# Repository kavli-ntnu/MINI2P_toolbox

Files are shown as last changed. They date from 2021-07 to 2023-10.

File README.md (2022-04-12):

# MINI2P_toolbox 
 
## Project:

MINI2P freely-moving calcium imaging and spatial tuning analysis

## Description: 

MINI2P_toolbox includes the codes, softwares, 3D models, protocols, and etc. for buidling and using MINI2P to do freely-moving recording. MINI2P is an open-source miniature 2-photon microsocpe for fast high-resolution calcium imaging in freely-moving mice, published in Zong, et al.,"Large-scale two-photon calcium imaging in freely moving mice (2022)". With the materials provided in this toolbox, people can assemble, test the MINI2P system, set up the animal tracking system, process the MINI2P imaging data, extract neuronal activity from single cells, and combine the neuronal activity data and the tracking data together for user-depedent downsteam analysis. The multi-FOV stitching software is also included. The codes for most of the anaylsis (grid cells, place cells, etc) in the paper "Large-scale two-photon calcium imaging in freely moving mice (2022)" are also provided.

## Contents: 

1) [Hardware](Hardware)

      [3D models (and 2D drawings for custom components)](Hardware) of all components for bulding a complete MINI2P system.


2) [Protocols](Protocols)

    a) [P1–Shopping and Machining list](https://github.com/kavli-ntnu/MINI2P_toolbox/blob/960fcab65f2849e5c8f486b81061c7c759f8e879/Protocols/P1%20-%20Shopping%20&%20Machining%20List%20.pdf). This document lists each essential component with the supplier, the product name, the model (or item reference) and its approximate price in Euro. 2D Drawings and 3D models of most components are available [here](https://github.com/kavli-ntnu/MINI2P_toolbox/tree/main/Hardware) .

    b) [P2-System building protocol](https://github.com/kavli-ntnu/MINI2P_toolbox/blob/main/Protocols/P2%20-%20System%20building%20protocol%20.pdf). This protocol includes all steps to assemble a MINI2P system. Each Protocol starts with a short-list of main reagents and tools needed, followed by an overview schematic of the module, and  a table with the main products.
       HC-920 assembly building and laser coupling video tutorial can be found on the [link](https://www.youtube.com/watch?v=HjAtoPbDu8E).    

    c) P3–Miniscope assembly protocol. How to assemble a MINI2P microscope is described in this protocol. Assembly tutorial video can be found on the [link](https://youtu.be/I0aYfi8GrIc). 

3) [Software](Software) 
      
      a) One scanimage Machine Data File (MDF) for [2000Hz MEMS-L scanner](Software/SI%20settings/Machine_Data_File_2000Hz.m). A second file for [5600Hz MEMS-F scanner](https://github.com/kavli-ntnu/MINI2P_toolbox/blob/main/Software/SI%20settings/Machine_Data_File_5600Hz.m)
      
      b) An example [Suite2P settings](Software/Suite2P%20options/GCaMP6S_P2_C1_7.25Hz_MEC.npy).
      
      c) Two DLC model configuration files:
      * [DLC1](Software/DLC%20model%20options/DLC1.yaml),
      * [DLC2](Software/DLC%20model%20options/DLC2.yaml),
      
      More details in [Documents](Documents/DeepLabCut-trained-Models.md).
      
      d) [AnimalTracker.vi](Software/AnimalTracker): a Labview program for recording animal behaviors and synchronizing the tracking camera recording with the MINI2P imaging. More details in [Documents](Documents/AnimalTracker.vi.md)
      
      e) [MINI2P SI device](https://github.com/kavli-ntnu/MINI2P_toolbox/tree/main/Software/MINI2P%20SI%20Device): Briefly, this device enables users to measure MINI2P distortion in different planes, do fast data correction, and register MINI2P system information in ScanImage software. And all this information is saved in Tiff header now.  Video tutorial can be found on the [link](https://youtu.be/DlftmRX5ty0).  More details in [Readme](https://github.com/kavli-ntnu/MINI2P_toolbox/blob/main/Software/MINI2P%20SI%20Device/Readme_20220322.docx)

4) [Analysis](Analysis)

      a) [Pipelines](/Analysis/Pipeline) for spatial tuning analysis included in the paper (grid cells, place cells,etc).

      b) [NATEX.mlapp](/Analysis/Applications/NATEX): Nat Explorer, an application to load, process and preview the neuronal activity data (from the Suite2P output) and the tracking data (from the DLC output). It also combines the neuronal activity data and tracking data into the NAT.mat (Neuron Activity aligned with Tracking Matrix) and put all necessasy information into ExperimentInformation.mat for the user-specific downsteam analysis. More details in [Documents](Documents/NATEX.mlapp.md) 
      

      c) [StitchingChecker.mlapp](Analysis/Applications/StitchingChecker): an application to stitch multiple FOV recorded from different positions of the cortext. It can load in wide-field image as a reference for FOV alignment and can also take the retinotopic mapping result in for identifying different visual cortices. The precise alginment of FOVs is confirmed by 
      
      * overlapping of the landmarks between FOVs and the wide-field image, or between neighbouring FOVS; 
        
      * peak cross-correlation between FOVs and the wide-field image, or between neighbouring FOVs;
        
      * overlapping of the repeated cells in neighbouring FOVS. We also found this application can be used to register imagings recorded in multiple days. 
          
      More details in [Documents](https://github.com/kavli-ntnu/MINI2P_toolbox/blob/main/Documents/StitchingChecker.mlapp.md)
     

     d) [DistortionCleaner.mlapp](Analysis/Applications/DistortionCleaner)： an application to elimiate the scanning distortion of MINI2P imaging, calibrate FOV and pixel size, and generate transform matrix. This program works similar to the ScanImage plugin “MINI2P distortion detecotion", but can work without installing Scanimage. Note that since the release of MINI2P SI Device in March, 2022, this function is not in use or maintenance any more. Users can still install and try it but we will not provide any support or bug-fix. More details in [Documents](Documents/DistortionCleaner.mlapp.md)
     

5) [Documents](Documents)

    a) [Requirements](Documents/requirements.md): A list of the non-optical components necessary to build and use a MINI2P system, including licencsed software requirements. 
    
    b) [How-to](Documents/readme.md): A set of more detailed how-to documentation about how some components of the system work. 

## Usage:

  Applications NATEX, StitchingChecker and DistortionCleaner were written with Matlab app designer. In order to use these software, please press "open” in the home toolstrip of Matlab, select the software, wait until the app designer interface pops out, and then press "run". Some details in how to use each application is provided under [Documents](Documents/readme.md)

## Credits: 

This repository was created by Weijian Zong and maintained by the [Moser group](https://www.ntnu.edu/kavli/moser-group#/view/about) at Kavli Institute for Systems Neuroscience. It has benefitted from the inputs of all authors of the paper Zong, et al.,"Large-scale two-photon calcium imaging in freely moving mice," _Cell_(2022). Sections of the analysis code are based on the [Behavioural Neurology Toolbox](https://bitbucket.org/cnc-ntnu/bnt), (c) Vadim Frolov 2018.

MINI2P is a complete open-source project, we encourage people to use, test, modify and further develop this toolbox. If you have any questions or suggestions, or find any bugs in the codes, please contact us or submit an issue. If you use the code or data, please cite us!

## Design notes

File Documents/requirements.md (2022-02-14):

# Requirements for the mini2p toolbox

## Hardware

Substituting alternative, comparable, pieces of hardware is generally possible. Modifications to the software will usually be required if so.

### Microscope

A complete bill of materials can be provided upon request. Details of specific hardware components of the microscope are discussed in the associated publication:

> W. Zong *et al*, "Large-scale two-photon calcium imaging in freely moving mice". [BioRXiv (2021)](https://doi.org/10.1101/2021.09.20.461015)

A single computer workstation is required for experiment control. Experimental control is not particular demanding of computing resources:
* Windows 10 x64
* Spare PCIe 3 x8 interface
* Spare PCIe 6-pin power connector

Post-recording imaging analysis via Suite2P and DeepLabCut is more demanding. Post-recording analysis does not need to take place on the same computer. 
* Version 11 Cuda compatible graphics card with >8GB vRAM
* Minimum 4GB RAM per CPU core, recommended 8GB.
* Minimum 4 cores. 

## Software

### Recording

* Matlab 2020b or more recent
  * [Mathworks](https://se.mathworks.com/)
* LabView 2020 or more recent
  * [National Instruments](https://www.ni.com/en-no/shop/labview.html)
  * [Anaconda](https://www.anaconda.com/products/individual)
* ScanImage 2020 Basic or more recent
  * The Free edition does not provide the necessary tools
  * [Vidrio](https://vidriotechnologies.com/compare-scanimage-version/)
* vDAQ RDI driver 2019-11-20 or more recent
  * SDK for the vDAQ interface card
  * [Vidrio](https://vidriotechnologies.com/drivers)
* Pylon 6.2.0 or more recent
  * Camera controller software for the Basler camera series
  * [Basler](https://www.baslerweb.com/en/sales-support/downloads/software-downloads/)
* PMT2100 4.0 or more recent
  * SDK for the Thorlabs PMT2100 photomultiplier tube
  * [Thorlabs](https://www.thorlabs.com/software_pages/ViewSoftwarePage.cfm?Code=PMT)

### Postprocessing

* Matlab 2020b or more recent
  * [Mathworks](https://se.mathworks.com/)
* Python 3.8 or more recent
  * Due to Suite2P's requirements, Anaconda and the Conda package manager are recommended
* DeepLabCut 2.2.0 or more recent
  * MachineMarkerless subject tracking
  * [Mathis Lab](http://www.mackenziemathislab.org/deeplabcut)
* Suite2p v0.10.0 or more recent
  * Two-photon imaging processing
  * [Pachitaru Lab](https://github.com/MouseLand/suite2p)

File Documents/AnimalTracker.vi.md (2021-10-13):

## Program location: 
MINI2P_toolbox/Software/AnimalTracker/
## Description: 
AnimalTracker.vi is a Labview program for recording animal behaviors, and synchronizing the tracking to the MINI2P imaging using a Basler camera. Currently, it was well validated by using camera acA2040-90um-NIR (https://www.baslerweb.com/en/products/cameras/area-scan-cameras/ace/aca2040-90um/). More validation will be published soon.
## Hardware requirement: 
1) Basler camera (recommend: [aca2040-90um](https://www.baslerweb.com/en/products/cameras/area-scan-cameras/ace/aca2040-90um/));
2) Basler camera [I/O cable](https://www.baslerweb.com/en/products/vision-components/cable/basler-gp-i-o-cable-hrs-6p-open-p-10-m/);
3) Basler cable [USB 3.0 Micro B](https://www.baslerweb.com/en/products/vision-components/cable/basler-cable-usb-3-0-micro-b-sl-a-p-3-m/);
## Software requirement: 
1) [NI-MAX](https://www.ni.com/en-no/support/downloads/drivers/download.system-configuration.html#371210)(20.0 or newer)
2) [Labview](https://www.ni.com/en-no/support/downloads/software-products/download.labview.html#369643)(2020 or newer)];
3) [NI-IMAQ](https://www.ni.com/en-no/support/downloads/drivers/download.vision-acquisition-software.html#367318);
3.1) [NI-IMAQmx](https://www.ni.com/en-no/support/downloads/drivers/download.ni-daqmx.html#409845);
3.2) [NI-IMAQdx](https://www.ni.com/en-no/support/downloads/drivers/download.vision-acquisition-software.html#367318);
4) (optional)[Pylon](https://www.baslerweb.com/en/sales-support/downloads/software-downloads/software-pylon-6-2-0-windows/) (6.2.0 or newer);
## Wiring:
To establish the correct camera wiring, first select Pins 2 and 5 of I/O cable which are Opto-coupled I/O input line and its ground, respectively. On the I/O cable, pins 2 and 5 are assigned as Pink and Grey, respectively. Link them with a BNC connector and plug the I/O cable from the camera to the vDAQ frame clock channel (one of the digital channels, in this case D3.7). See Fig. (1) for illustration.
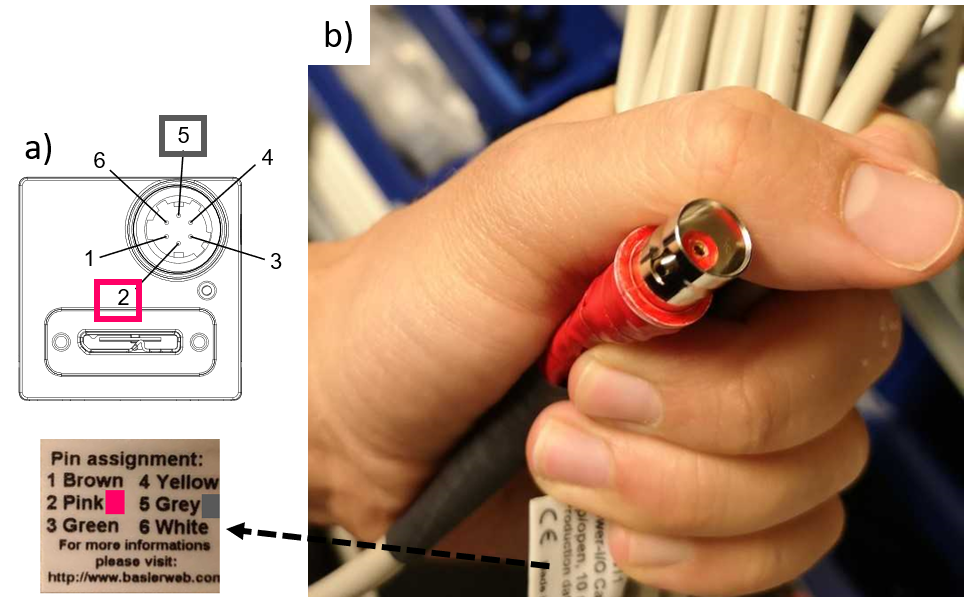
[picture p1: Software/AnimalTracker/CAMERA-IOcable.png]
Schematic of I/O cable pins and labelling used to connect the Animal Tracker camera


The Basler camera is working in External Trigger Mode, meaning it starts as soon as it gets a signal (0-5V) via input cable from the vDAQ (Start focus or grab in Scan Image, which sets up the Animal Tracker).
## Installation: 
The necessary drivers are those mentioned in Software Requirements from NI-MAX and NI-IMAQ. Pylon drivers are not needed, unless one wishes to visualize the camera using Pylon Software. In that case, USB 3.0 drivers should be installed.
### main pragram
To start-up, open the Virtual instrument application (.vi file) entitled "AnimalTracker.vi", and a graphical user interface will display as follows:

## GUI:
![Schematic of Animal Tracker GUI overview]
(https://github.com/kavli-ntnu/MINI2P_toolbox/blob/4a45033ba603d2f39251690c86131b548938de0d/Software/AnimalTracker/AnimalTracker-overview.png)

## Usage:
### change the default frame size, frame rate, exposure time and gain
1. On the same Directory where the imaging files are going to be saved, create an empty text file (in this case, "1.txt"). 
2. On the top left panel (see nr 1), select that text file created.
3. Chose Trigger Mode "External" and update frame rate (14.5 Hz) as well as other parameters as shown.
4. Finally, on the left bottom part, choose the camera type "1" for bottom and "2" for Top, and other relevant information which is going to be attached to a .csv file as:

###
## Output:

## .tiff to .mp4 conversion

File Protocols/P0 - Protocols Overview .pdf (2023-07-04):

## Protocols Overview

### P1 – Shopping and Machining list

This document lists each essential component with the supplier, the product name, the model (or item reference) and its approximate price in Euro. 2D Drawings and 3D models of
most | components | are | available | on | Github | (https://github.com/kavli-
ntnu/MINI2P_toolbox/tree/main/Hardware). (https://github.com/kavli-ntnu/MINI2P_toolbox/tree/main/Hardware)

### P2 – System building protocol

This protocol includes all steps to assemble a MINI2P system. Each Protocol starts with a short-list of main reagents and tools needed, followed by an overview schematic of the module, and a table with the main products.
HC-920 assembly and laser coupling video tutorial can be found on the link: https://www.youtube.com/watch?v=vo_EgYPYI24&list=PLonWNO9SywvJXpIgQEp6jQMSh_jrn_jPU&index=3&t=4s. (https://www.youtube.com/watch?v=vo_EgYPYI24&list=PLonWNO9SywvJXpIgQEp6jQMSh_jrn_jPU&index=3&t=4s)

### P3 – Miniscope assembly protocol

How to assemble a MINI2P microscope is described in this protocol. Assembly tutorial video can be found on the link: https://www.youtube.com/playlist?list=PLonWNO9SywvJXpIgQEp6jQMSh_jrn_jPU.

### GFB assembly protocol

This protocol describes the steps to assemble the GRIN-end fiber bundle (GFB), which replaces the tapered fiber bundle (TFB) as the main fiber collecting and relaying the emission signal to the detection module.

### MEMS wires and mirror protocol

This protocol includes the main steps for MEMS wires assembly and soldering of the MEMS mirror flex cable. Soldering MEMS flexcable can be found on the link: https://www.youtube.com/watch?v=ghV1DY1aKAA&list=PLonWNO9SywvJXpIgQEp6jQMSh_jrn_jPU&index=1 (https://www.youtube.com/watch?v=ghV1DY1aKAA&list=PLonWNO9SywvJXpIgQEp6jQMSh_jrn_jPU&index=1)

The MINI2P video tutorial package can be found on the link: https://www.youtube.com/playlist?list=PLonWNO9SywvJXpIgQEp6jQMSh_jrn_jPU

Besides the video-tutorials above, it also includes:
- ScanImage tutorial:
https://www.youtube.com/watch?v=uUZ1o5XFiwU&list=PLonWNO9SywvJXpIgQEp6jQMSh_jrn_jPU&index=2&t=714s (https://www.youtube.com/watch?v=uUZ1o5XFiwU&list=PLonWNO9SywvJXpIgQEp6jQMSh_jrn_jPU&index=2&t=714s)
- SI device for distortion, detection, and correction: https://www.youtube.com/watch?v=4hNTMCyMdrM&list=PLonWNO9SywvJXpIgQEp6jQMSh_jrn_jPU&index=5&t=59s (https://www.youtube.com/watch?v=4hNTMCyMdrM&list=PLonWNO9SywvJXpIgQEp6jQMSh_jrn_jPU&index=5&t=59s)

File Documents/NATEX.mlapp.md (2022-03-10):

## Application location:

[NATEX.mlapp](https://github.com/WeijianZong/MINI2P_toolbox/tree/main/Analysis/Applications/NATEX)
## Description:
One recording in a freely-moving experiment using MINI2P system usually includes one or multiple MINI2P calcium imaging files (tiff stack) generated by [ScanImage](https://vidriotechnologies.com/scanimage/) and one or multiple animal tracking videos generated by tracking camera recording software, such as [AnimalTracker](https://github.com/WeijianZong/MINI2P_toolbox/wiki/AnimalTracker.vi) or [Pylon](https://www.baslerweb.com/en/sales-support/downloads/software-downloads/software-pylon-6-2-0-windows/). Becuase the MINI2P imaging and tracking video recording in our system is [hardware-level synchronized](https://github.com/WeijianZong/MINI2P_toolbox/wiki/NATEX.mlapp#synchronization-and-frame-rate), the synchronization data is not required.

In order to implement quantitative analysis for real neuroscience studies, individual cells' anatomical and activity information, and animal behavior including trajectory, speed, and head direction need to be extracted from the raw imaging tiff files and tracking videos, respectively. 

First of all, we use [Suite2P](https://suite2p.readthedocs.io/en/latest/) to do cell segmentation, signal extraction, and signal deconvolution from raw calcium imaging tiff stack, and [DeepLabCut](https://suite2p.readthedocs.io/en/latest/) to extra animal`s body parts, like ears, body center, tail base, and etc., from raw animal tracking video. Still, the output of Suite2P and DeepLabCut can not be directly used for biology analysis until a more meaningful, highly extracted and integrated, and easy-to-understand data format is generated. And a powerful data visualization tool for non-programming-expert to easily present and investigate these data before going into a more complex analysis is also required. NATEX.mlapp was developed for these purposes. It has four major functions:

1) Process [Suite2P output](https://github.com/WeijianZong/MINI2P_toolbox/wiki/NATEX.mlapp#suite2p-output): take the output from Suite2P, calculate dF/F, significant transients, and SNR, clear up the deconvolved signal, detect repeated cells in multiplane imaging data, and finally package the processing information and save processed neuron activity data.
2) Process [DeepLabcut output](https://github.com/WeijianZong/MINI2P_toolbox/wiki/NATEX.mlapp#deeplabcut-output): Take the output from DeepLabCut, calculate head/body position, speed, direction using user-selected tracking models, combine or split multiple recording sessions, and finally package the processing information and save processed tracking data. 
3) Integration: combine the processed neuron activity data and tracking data with a user-defined alignment strategy, package the combination information, and save the combined data. 
4) Data Visualization: provide multiple useful functions to view the neuronal activity (dF/F, significant transients, or deconvolved signal), different types of anatomical cell map, MINI2P imaging projection, animal trajectory derived by head or body (coded by position, speed, direction), the spatial tuning plots ( calcium event/position plot, activity map, calcium event/direction/position plot, directional tuning), etc.
The simplified data-flow chart and NATEX major functions are shown below:

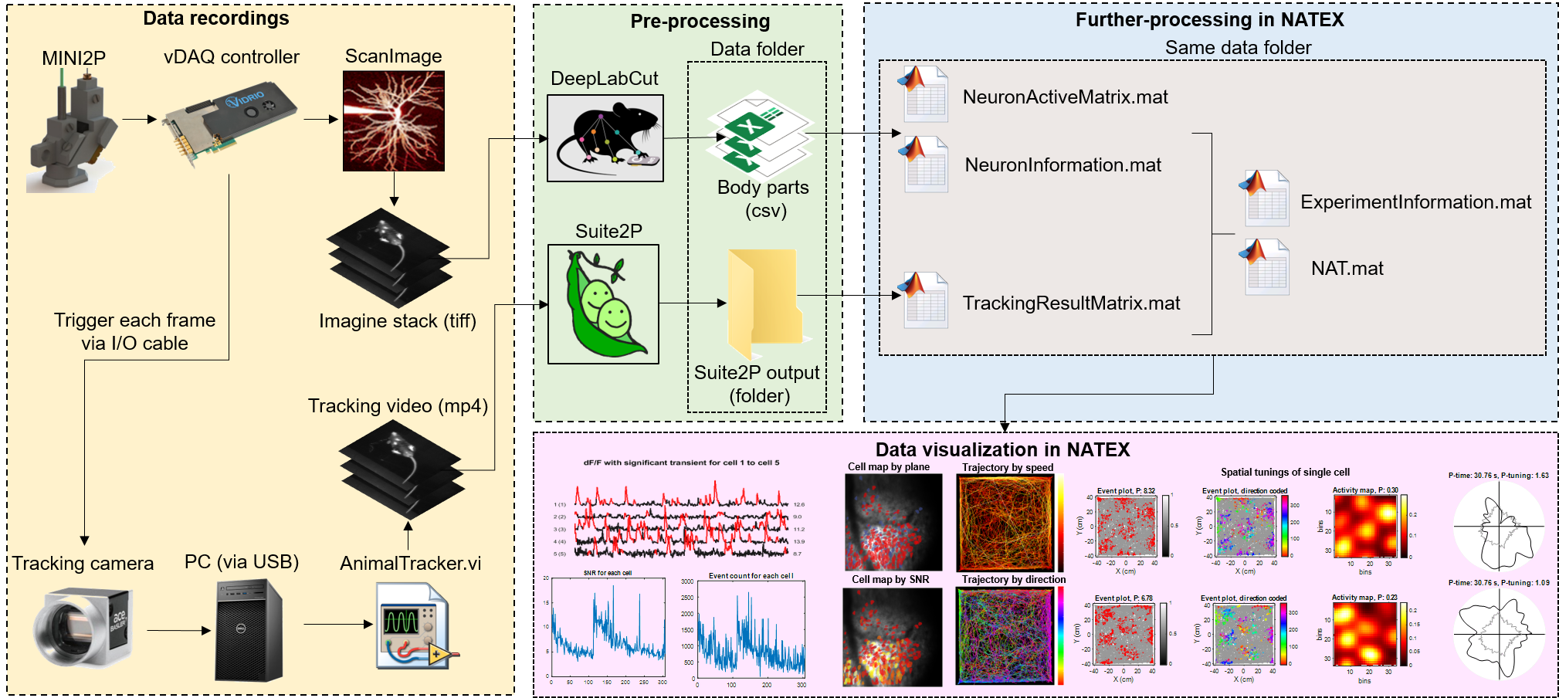
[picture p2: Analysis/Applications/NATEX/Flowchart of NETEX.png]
Schematic of the data flow from the raw data recording to the output of NATEX


NATEX.mlapp is highly modularized so you can input, process, view, output, and reload (processed) neuronal activity data, tracking data, or combined data independently. 

The Python version of NATEX will be published in the first KISN International MINI2P workshop in 2022.

## Installation:

### Matlab and toolbox
The app was written with Matlab 2020a, but should work with any newer version. It uses the Statistics and Machine Learning Toolbox, the DSP System Toolbox and the Curve Fitting Toolbox, which need to be installed before running the applications.

### Install application
There are two ways to install the application.

First way is to install the raw codes which gives you the right to modify the function:

Download or clone the whole repository in a local folder. Open Matlab, press "set path” on home toolstrip, then press “add with subfolders...", navagate to the location of \MINI2P_toolbox\MINI2P_toolbox\AnLysis, press "select folder", and finally, "save" the current path.

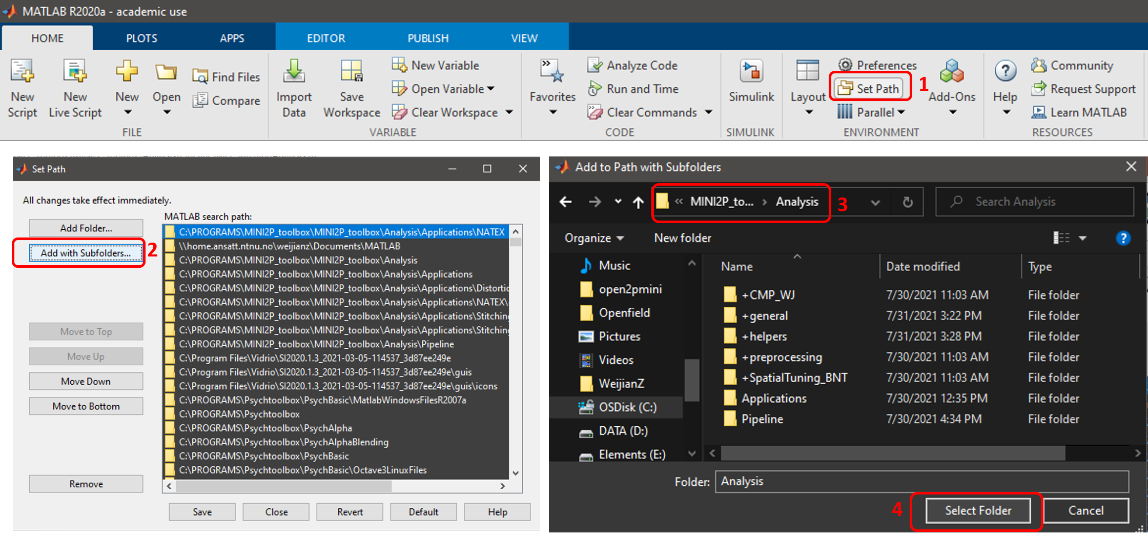
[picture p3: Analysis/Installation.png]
Installation


Second way is to install the app into the Matlab toolboxes which makes the most convinient way to call it. But you can not see or change the codes:

### Install ScanImage
In order to read out and save the ScanImage tiff header (the function "Save SI Information"), you need to install ScanImage on the same computer too. The free version will work well. Follow their [instruction](https://vidriotechnologies.com/scanimage/) for installation.

## Input format and organization:

### Directory structure
All recordings belong to one experiment should be put in one "data folder". An experiment can include multiple sessions and in each session, the raw data usually includes one tiff-stack file from MINI2P recording (output from ScanImage) and one tracking video (.AVI). For analyzing neuronal activity data, you should first run Suite2P analysis on your raw tiff files. Suite2P will automatically combine all tiff files in the "data folder" together to extract the cell signal and generate a single output folder called "suite2p". Folder "suite2p" is the only thing NATEX.mlapp needs to process the neuronal activity data. Therefore, do not change the name of this folder after it is generated by Suite2P. In addition, important to make sure that the option "save_mat" is 1 and the option "combined" is 1 when you run the Suite2P analysis. If you want to also extract and output the ScanImage tiff header (when the function "Save SI Information" is enabled), keep the raw tiff files in the "data folder" too. For analyzing tracking data, you will first run DeepLabCut (or other method or software) to extract the body part position. DeepLabCut will generate one set of results for each video (or session). NATEX.mlapp only looked for and takes the CSV files that include all body-part tracking results to do the tracking analysis. In other words, as soon as you can generate CSV files with the same format as DeepLabCut, they can be read by NATEX.mlapp for analysis. The number of sessions is decided by the number of tracking files (.csv) the user selects. 

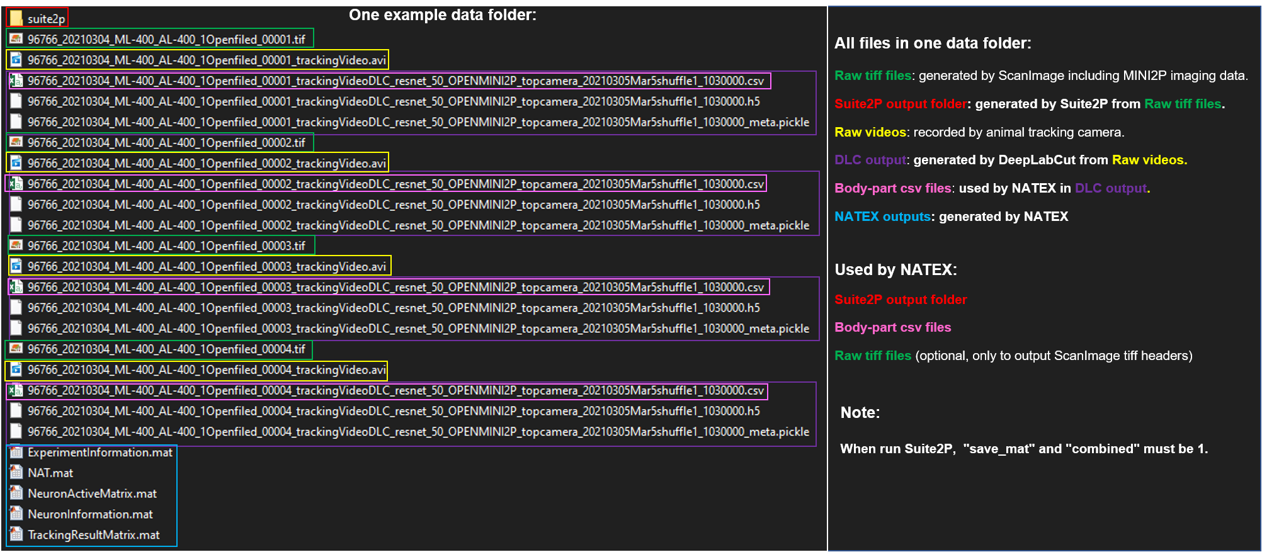
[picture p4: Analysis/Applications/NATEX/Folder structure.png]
Folder Structure


### Session definition
### Modularity
NATEX is coded with high modularity which means the neuronal activity analysis and tracking analysis are quite independent. Therefore, it does not require all kinds of input to run specific analyses. For example, if you select the analysis type as " [Only MINI2P](https://github.com/WeijianZong/MINI2P_toolbox/wiki/NATEX.mlapp#only-analyze-calcium-activity-data-mini2p-imaging) ", you only need to have the Suite2P output folder. And if you select " [Only tracking](https://github.com/WeijianZong/MINI2P_toolbox/wiki/NATEX.mlapp#only-analyze-tracking-data) ", you only need the body-part CSV files. This is useful for some pilot experiments such as head-fixed test recordings or pure behavior studies in which, tracking video or MINI2P imaging files is not applicable, respectively.

## Output format and organization:
In total, NATEX will generate five output files. NeuronActivityMatrix.mat and NeuronInformation.mat are generated if the analysis type is "Only MINI2P" "MINI2P+tracking" or "Complete pipeline". TrackingResultMatrix.mat is generated if the analysis type is "Only Tracking ", "MINI2P+tracking" or "Complete pipeline". NAT.mat and ExperimentInformation.mat are generated if the analysis type is "Complete pipeline", or manually execute the function "generate NAT!". All these files are saved in the same data folder.

### NeuronActivityMatrix.mat
NeuronActivityMatrix.mat is generated after the neuronal activity analysis part in analysis type "Only MINI2P" "MINI2P+tracking" or "Complete pipeline" is finished. It included several cell-by-cell signal traces described in detail below: 
### NeuronInformation.mat
NeuronInformation.mat is also generated after the neuronal activity analysis part in analysis type "Only MINI2P" "MINI2P+tracking" or "Complete pipeline" is finished. It included cell footprints, SNR, event counting, processing parameters, and all other useful analysis information other than the signal traces that are saved in NeuronActivityMatrix.mat already. Described in detail below: 
### TrackingResultMatrix.mat
TrackingResultMatrix.mat is generated after the tracking analysis part in analysis type  "Only Tracking ", "MINI2P+tracking" or "Complete pipeline" is finished. It included the head (or body if selected) position, direction and speed information, tracking processing parameters,and all other useful analysis information. This is the only output in tracking analysis part. Described in detail below: 
### NAT.mat
NAT.mat is generated after the neuronal activity data and tracking data combination part in analysis type "Complete pipeline", or manually executed function "generate NAT!" is finished. It is a matrix that combines cell-by-cell neuronal activity data and animal tracking data.Described in detail below: 
### ExperimentInformation.mat
ExperimentInformation.mat is also generated after after the neuronal activity data and tracking data combination part in analysis type "Complete pipeline", or manually executed function "generate NAT!" is finished. Most of the information saved here are copied from NeuronInformation.mat and TrackingResultMatrix.mat. But it also includes the neuronal activity data and tracking data combination and alignment information that is unique here. Described in detail below: 

## GUI:
### Overview
There are 11 permanent panels on GUI and a pop-up will appear when a certain preview button is pressed (described in detail below). Currently, all options and parameters will be saved in output data files (.mats) and updated automatically when processed data is loaded in. In the future version, NATEX will allow the user to save and load in analysis options and parameters without specific processed data.
### "Data input" panel
In this panel, user selects the desired analysis type and the data folder. In the future version, user can also save and load in analysis options and parameters in this panel.
1. "Analysis type": a drop-down allows users to select analysis type.
2. "Select data folder and DLC output": when press this button, a folder-selecting dialog box appears for the user to select the data folder. if the analysis type is "Only Tracking ", "MINI2P+tracking" or "Complete pipeline", a second dialog box appears after the data folder is selected, for the user to select tacking CSV files. Users should select "all" csv files that they want to analyze and combine with neuronal activity data.
### "Control" panel
In this panel, user controls the start and abort of the analysis.
1. "Run analysis!": start the analysis based on user-selected analysis type.
2. "Abort analysis": manually abort the analysis. Attention! You may get some incomplete results or output when aborting the analysis. Errors may also appear if you use other functions after aborting an analysis. Therefore, always run the analysis again after you abort the last analysis.
3. "Close all figures": all pop-ups will be closed.
### "Options for neuronal activity analysis" panel
In this panel, user needs to decide several options for processing and analyzing the neuronal activity data. The reason and reference for these parameters can be found in the original paper (Zong, et.al, 2021).
1. "Moving window": The time window to calculate the local standard deviation of the raw fluorescence. This local standard deviation is then used to compute the baseline fluorescence (F-zero). See [ΔF/F](https://github.com/WeijianZong/MINI2P_toolbox/wiki/NATEX.mlapp#%CE%94ff) calculation for details.  Default: 30s.
2. "Transient lasting": the temporal lasting threshold for a transient to be called a "significant transient". See [Significant transient](https://github.com/WeijianZong/MINI2P_toolbox/wiki/NATEX.mlapp#significant-transient) calculation for details. It depends on the calcium indicator dynamics and the signal quality. Default: 0.75s for GCaMP6s transgenic mice.
3. "Lowpass filter": the cut-off frequency of a low-pass filter applied on cell signal (ΔF/F) for calculating the cross-correlation between cells. It is not applied to the output data or any downstream analysis. Default: 2Hz.
4. "Neuropil correction": neuropil coefficient, the definition is the same as [neucoeff](https://suite2p.readthedocs.io/en/latest/settings.html#spike-deconvolution) in Suite2P. Default: 0.7. 
5. "Transient extent": a safe margin added on both sides of a significant transient so it can fully cover the deconvolved events. Default: 0.4s.
6. "Cell distance threshold": the distance threshold (unit: pixel) for two cells to be identified as [the same cell in different planes](https://github.com/WeijianZong/MINI2P_toolbox/wiki/NATEX.mlapp#same-cell-in-different-planes). Default: 10 pixels.
7. "Cell cross-correlation threshold": the cross-correlation threshold (unit: a.u.) for two cells to be identified as [the same cell in different planes](https://github.com/WeijianZong/MINI2P_toolbox/wiki/NATEX.mlapp#same-cell-in-different-planes). Default: 0.5.
8. "Cell overlap ratio threshold": the overlap ratio threshold (unit: a.u.) for two cells to be identified as [the same cell in different planes](https://github.com/WeijianZong/MINI2P_toolbox/wiki/NATEX.mlapp#same-cell-in-different-planes). Default: 0.75.

### "Cell selection" panel
This panel is for selecting a subgroup of cells to show in pop-ups such as activity traces, cell footprints, and spatial tuning plots. NATEX supports two modes of defining selected cells:
1. "Range": give the total number of cells ("cells to check") and the "start cell". For example, "cells to check"=5 and "start cell"=4 aims to show cells with ID: 4,5,6,7, and 8.  
1. "Arbitrary": directly input the cell ID. The separator can be comma(","), semicolon (";"),blank(" "), or tab (" "), and should be consistent. Do not put any separator at the end. For example: 1,2,3 

Note: NATEX only inputs and processes ROIs extracted and classified  "cells" in Suite2P. Therefore, the cell ID used here is not the same cell ID used in Suite2P. The Suite2P cell ID of each cell can be found in the file NeuronInformation.mat and is also shown on the cell map if the option "show cell ID" is selected.

### "Neuronal activity analysis result preview" panel
This panel is for viewing the neuronal activity processing analysis result. 
Read-only results:
 1. "X pixel" and "Y pixel": frame size of the 2P imaging.
 2. "channels": number of imaging channels.
 3. "planes": number of imaging planes.
 4. "Frame rate": sampling rate (per frame). 
 5. "Volume rate": "Frame rate"/"planes".
 6. "Total volumes": the number of stacks in the recording. If the recording is a single plane recording, this number is equal to the total number of frames. If the recording is a multi-plane recording, this number is equal to the total number of frames deciding the number of planes.
 7. “Total cells": number of cells classified as "cells" in Suite2P.
 8. "Repeated cells": cells that are identified as repeated recorded in multiple planes. For instance, if cell 1 in plane 1, cell 2 in plane 2, and cell 3 in plane 3 are identified as the same cell, and cell 2 has the highest SNR, then cell 1 and cell 3 are the repeated cells so that "Repeated cells" will add 2.

Show activity traces:

### "Options for tracking analysis" panel
This panel is used to define the parameters used for the tracking analysis.
 1. "Session combined?": tick this if the raw tiff files (ScanImage output) are blocks of the same session. If the individual tiffs in the base folder represent different session leave box unticked.
 2. "Tracking synched with MINI2P?": Tick this box if the tracking tiffs are synchronised with the scanImage output; meaning that the first frame of the tracking occurred at the same time as the the first frame of the calcium imaging. 
 3. "Track body": tick this box if the deep lab cut model used analysed body position and you want to track the body of the animal in addition to the head (it is possible to get an accurate occupancy trace by only track the head position of the animal). 
 4. "Tracking frame rate": exact frame rate used to record the animal's behaviour.  
 5. "Speed smooth":
 6. "Center x (pixel)" and Center y (pixel): the x and y pixel in the tracking tiffs corresponding to the centre of each image (also found in MetaData.csv if using custom LabView GUI)
 7. "Resolution (cm/pixel)": the resolution of the tracking images, in cm/pixel, used to calculate speed/distance etc.
 8. "Head tracking fashion": M1-M3 denotes the method used to calculate the head position/the way it is reported in the DLC output. M1 uses tracking of two points at equal distance from a centre point that is then used as the head position (e.g. left and right ear), where head direction is extrapolated as perpendicular from the line connecting the right and left point. M2 calculates head position as the centre of two parallel points anterior and posterior of the head position (e.g. nose and back of head), head direction is considered as the continued direction through these two points (ahead of the anterior point). M3 uses only one point to calculate head position and therefore does not have an accurate frame by frame head direction. The CSV column for each point in each of the methods denotes the actual column the x and y position of said point can be found in the DLC .csv output. 
9. "Body tracking fashion": M1-M2 specifies the method used to calculate body position. M1 uses two points on one line (e.g. head and tail base), whose anterior extension denotes the body direction. M2 uses a single position to track body position, body direction is therefore not applicable. The CSV column for each point in each of the methods denotes the actual column the x and y position of said point can be found in the DLC .csv output. 

### "Tracking and combined plots options" panel
This panel is used to input the options for the tracking and combine tuning maps. 
 1. "Angle bin (degree)": angular bins (in degrees) used for the tuning maps.  
 2. "Angle smoothing (degree)": degree(s) used for angular smoothing of tuning maps.
 3. "Plot range min (cm)":
 4. "Plot range max (cm)":
 5. "Min time (s)": 
 6. "Spatial bin (cm)": 
 7. "Spatial smoothing (cm)":
 8. "Speed threshold max (cm/s)":
 9. "Speed threshold min (cm/s)":
 10. "Show part": drop down menu to choose which body part to use for the tracking - head or body (often head gives the best tracking result). 
 11. "Tracking and tuning colormap": drop down menu to choose the colormap of the tracking maps used in next panel. Code can be manually be updated to incorporate whichever colormap the user chooses.   

### "Tracking analysis result preview" panel
This panel allows you to quickly look at the tracking data in terms of trajectory/direction/speed etc. 
 1. "Total sessions": read only result, shows the total amount of sessions found in the base folder.
 2. "Show session": drop down menu to decide which of the total number of sessions (as seen above) that will be plotted in this panel. 
 3. "Refresh": refreshing the panel. 
 Read only results:
 4. "Total frames": total number of frames for the individual session (not total amount if more than one session).
 5. "Total time": total time for individual session in seconds. 
 6. "Total distance (cm)": total distance covered by the animal the specified session.
 7. "Mean speed (cm/s)": average speed of the animal the specified session. 
 8. "90th speed (cm/s)": 90th percentile of speed that session. 
 9. "Show trajectory": button that shows the trajectory of the animal based on the inputs in this and "Tracking and combined plots options" panel. 
 10. "Show direction plot": button to open a figure showing the radial map of the head/body direction based on parameters set in panel input. 

### "NAT generation" panel
### "NAT result preview" panel
### "status monitoring" panel
### Pop-ups

## Usage:
### Run complete pipeline
### Only analyze calcium activity data (MINI2P imaging)
### Only analyze tracking data
### Only run data combination (generate NAT)
### Load in processed data
### Data visualization
## How it works
### ΔF/F
### Significant transient
### Deconvolution clear-up
### SNR
### Same cell in different planes
### Compute head/body position/direction/speed from body parts
### Synchronization and frame rate
### DLC and Suite2P alignment and session combination
## Warm up with the demo data

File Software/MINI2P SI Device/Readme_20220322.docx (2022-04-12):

Copyright:

Version1: (2022.03.22) at Kavli Institute, Trondheim, NTNU

The MINI2P distortion detection and correction method is from the paper Zong, et.al,Cell,2022

The MINI2P distortion detection GUI was written by Weijian Zong in the Moser lab

The SI device of MINI2P was modified from standard device in SI by Weijian Zong in the Moser lab, Mitchell Sandoe and Jacob Franklin in Vidrio Technologies, LLC

Updated version of this device and the user manual can be found in https://github.com/kavli-ntnu/MINI2P_toolbox

Copyright (C) 2021 Vidrio Technologies, LLC

ScanImage (R) 2021 is a software to be used under the purchased terms

Code may be modified, but not redistributed without the permission of Vidrio Technologies, LLC

Dependency:

1 Matlab: 2019b or later;

2 ScanImage: basic or Premium, 2021 or later;

3: Matlab toolbox “ Image Processing toolbox” : before installing “MINI2P”, please check inf image processing toolbox is installed. The method to check is shown below:

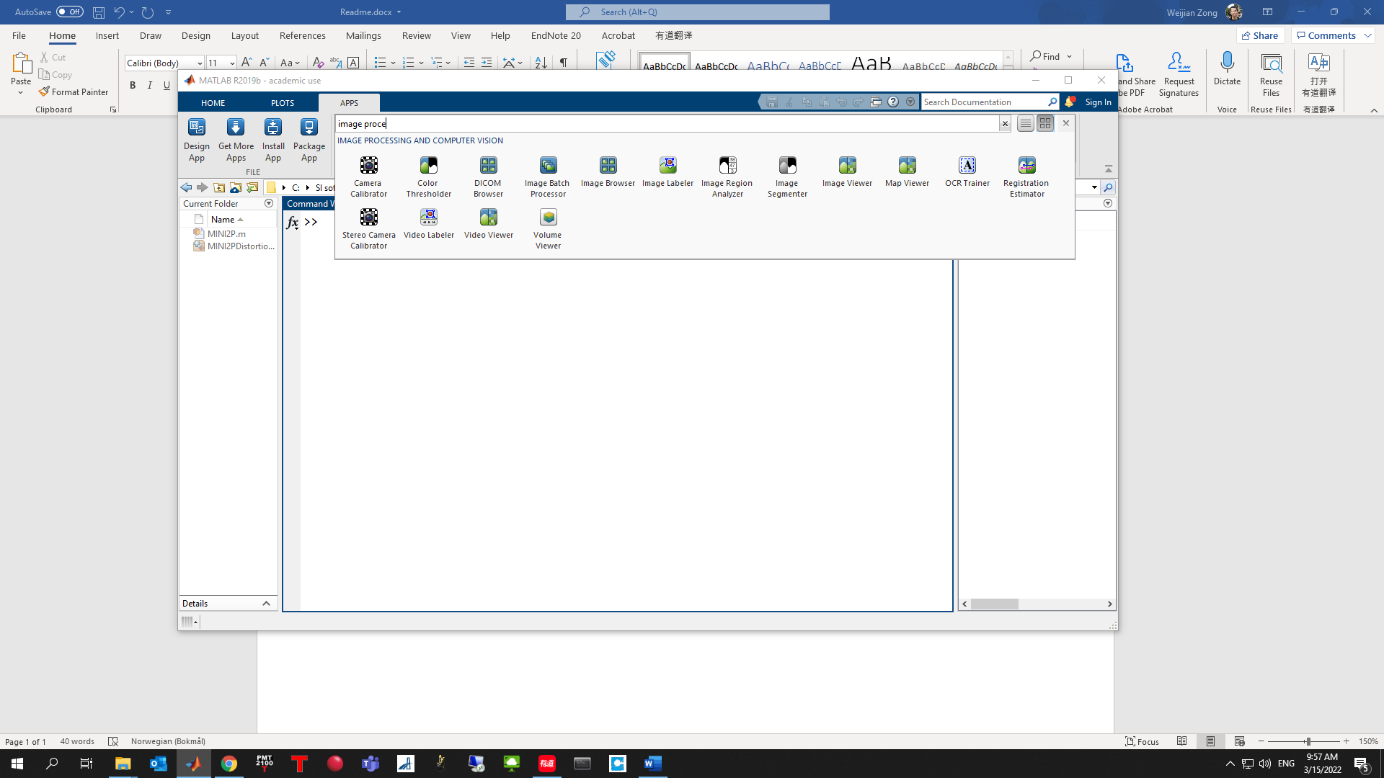
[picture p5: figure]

This figure shows where you can find the Imaging Processing toolbox in Matlab.

Installation:

1. Copy the entire folder “plugin” to SI root folder.

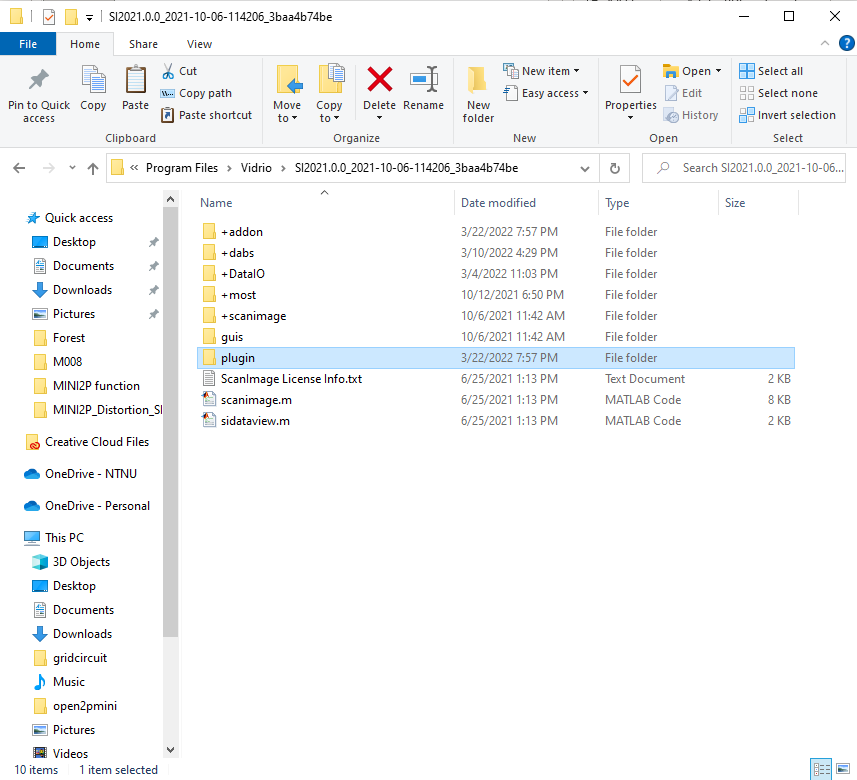
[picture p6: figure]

2. Copy the entire folder “+mini2p” to SI folder\+dabs\;

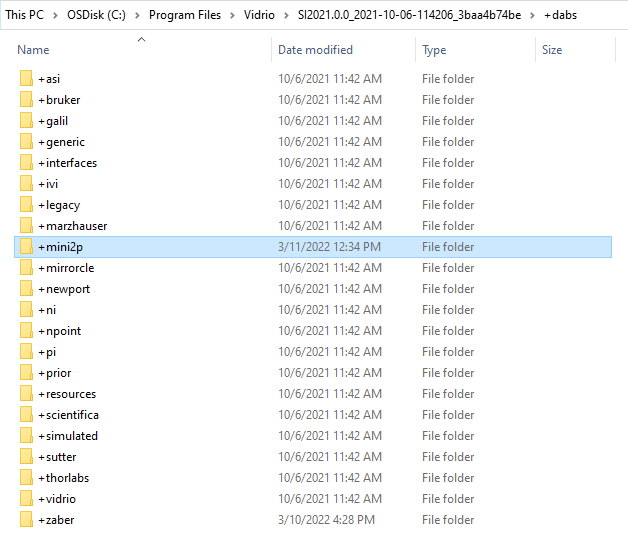
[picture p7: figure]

3. Copy file “MINI2PPage.m” to SI folder\+dabs\+resources\+configuration\+resourcePages\;

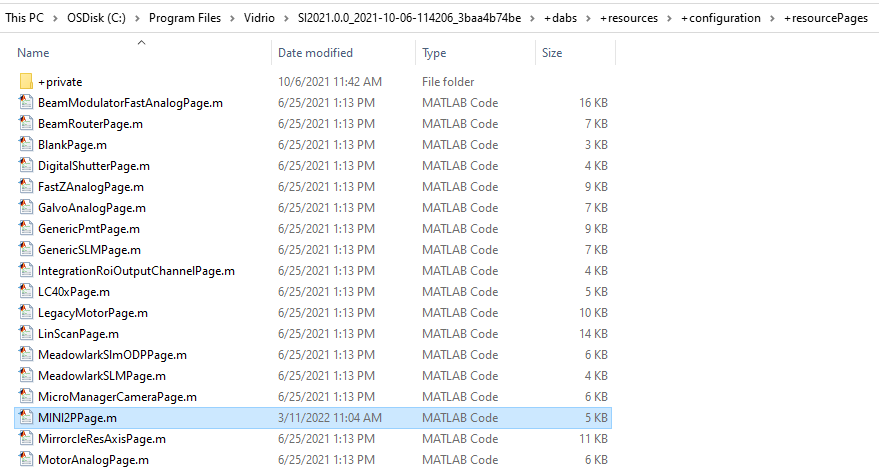
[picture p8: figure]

4. Copy file “MINI2PWidget.m” to SI folder\+dabs\+resources\+widget\+widgets\;

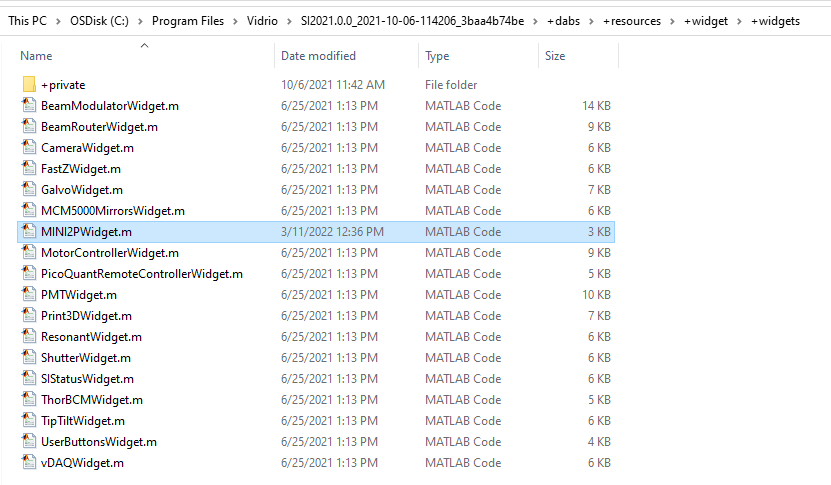
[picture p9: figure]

5.When starting ScanImage from Matlab, go to Machine Data File Editor, select “Devices”, press “+”, and select “Miscellaneous” → “MINI2P”. Then give a name to this device, i.e. “MINI2P tools”.

Note. Before installing the MINI2P, please make sure there is only one version of ScanImage installed.

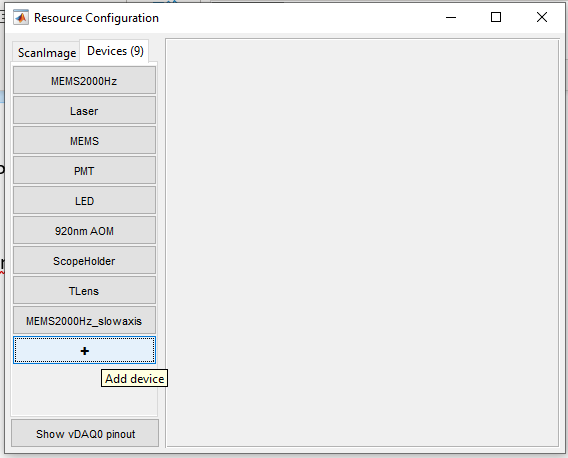
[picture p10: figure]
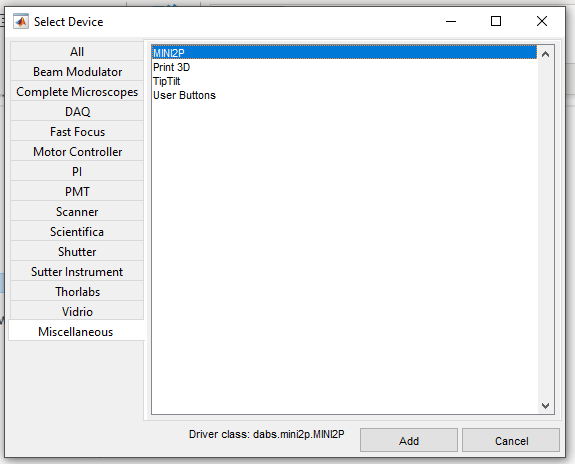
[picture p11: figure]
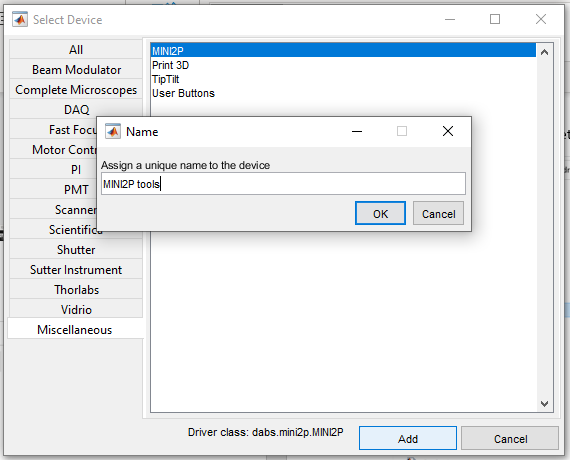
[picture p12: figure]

6 When the MINI2P device appears on Machine Data File Editor. It asks you to fill in the transform matrix (leave it empty if this is the first time you install MINI2P), MINI2P system name, MINI2P microscope name, and the objective type. This information can be found in MDF of ScanImage. This information will also be registered into the SI tiff header when you apply distortion correction in your future recording (see bellow). A MINI2P widget will also appear on your Widget Bar.

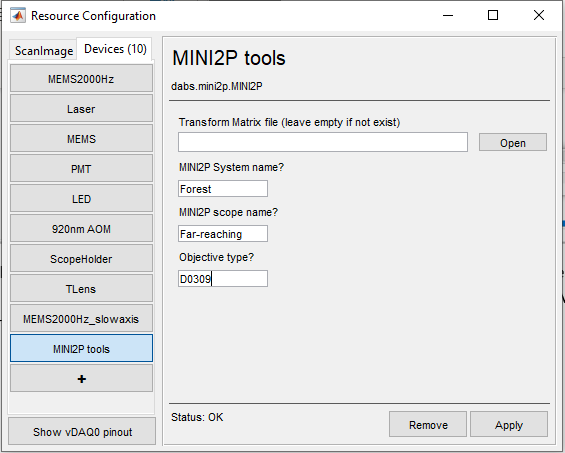
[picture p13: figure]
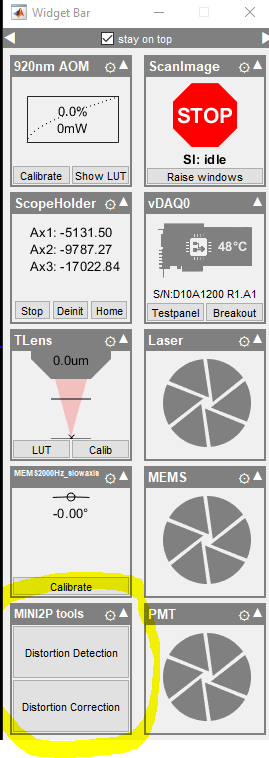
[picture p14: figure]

This figure shows the information registered in MDF when you successfully install MINI2P device.

Note: during the installation, it will automatically install the app “MINI2PDistortionDectction” in Matlab toolboxes. Please check if this app is successfully installed.

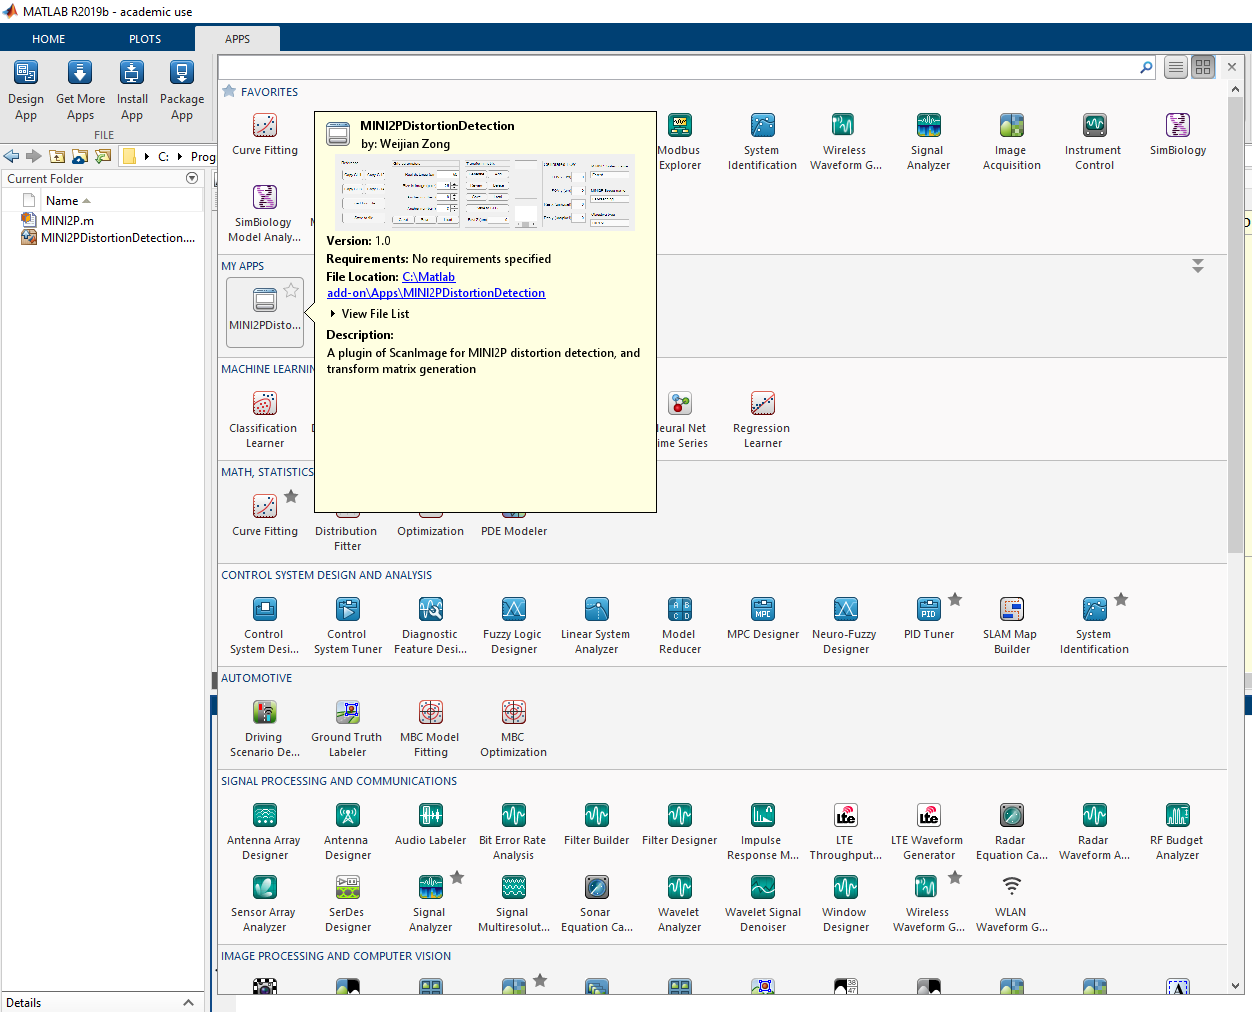
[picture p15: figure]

This figure shows where you can find the MINI2PDistortionDetection app in Matlab.

Usage:

1. Distortion Detection.

Summary:

This function is used to measure the distortion in the raw MINI2P image and generate a series of transformation matrices for correcting distortion in different focal planes. It was written in MATLAB App Designer and is called directly in ScanImage Device “MINI2P” via the button “Distortion Detection” on the MINI2P widget.

Steps for measuring distortion in different focal planes:

1 Open GUI: Press the button “Distortion Detection” on the MINI2P widget (left image below). An interface as that shown on the right should appear.

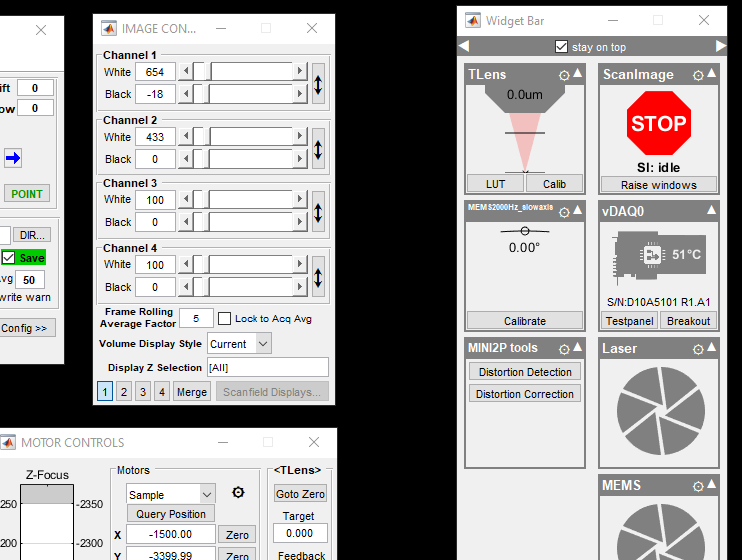
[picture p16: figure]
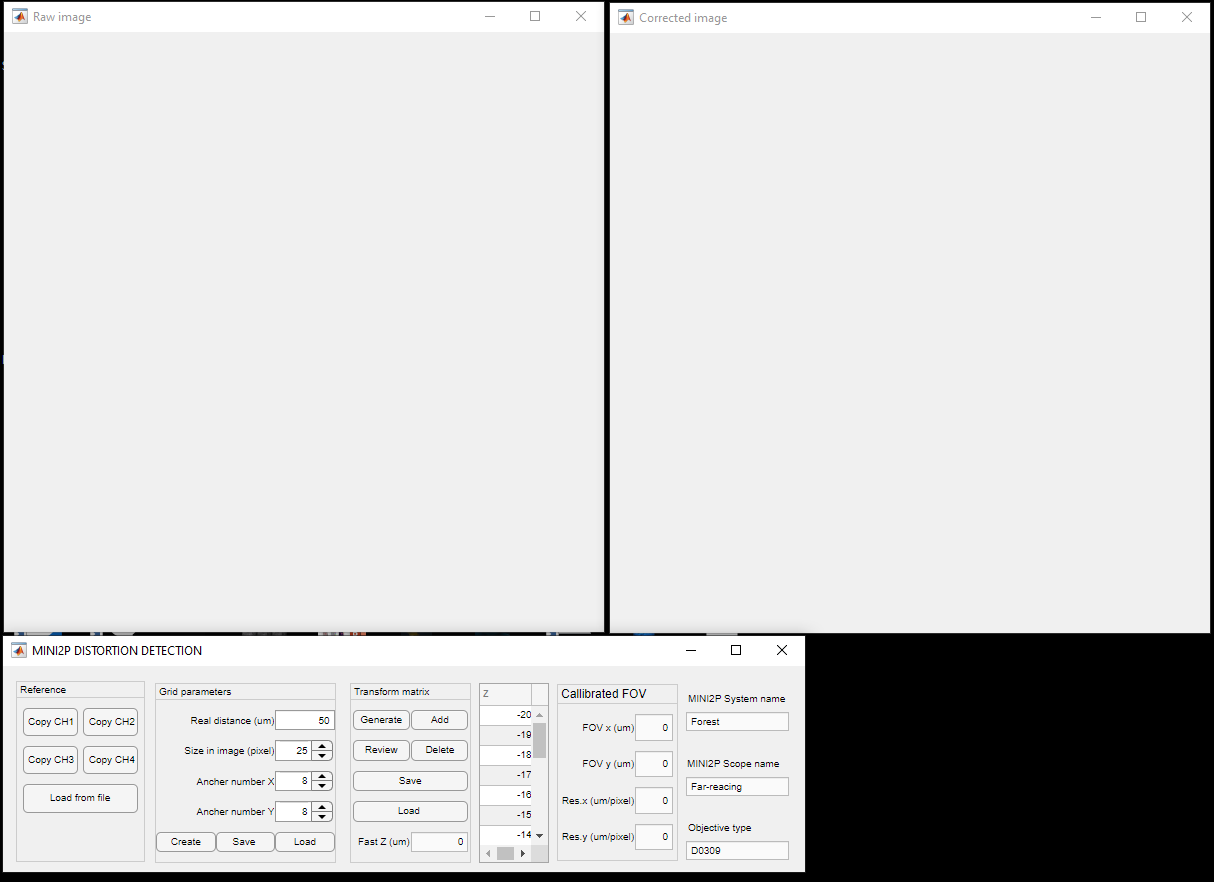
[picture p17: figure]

2 Load in reference image: Load in the image you want to use for creating the distortion matrices. We typically image a fluorescent grid sample where each intersection point is located 50 μm from the next, and all horizontal lines are arranged orthogonally on the vertical lines. The captured image will thus show directly how the microscope distorts the image. The reference image can either be copied directly from the ScanImage display (e.g. “Copy CH1”) or loaded from your computer (“Load from file”). The distortion correction code will assume that the zoom and focal plane of the image have the values currently set in ScanImage.

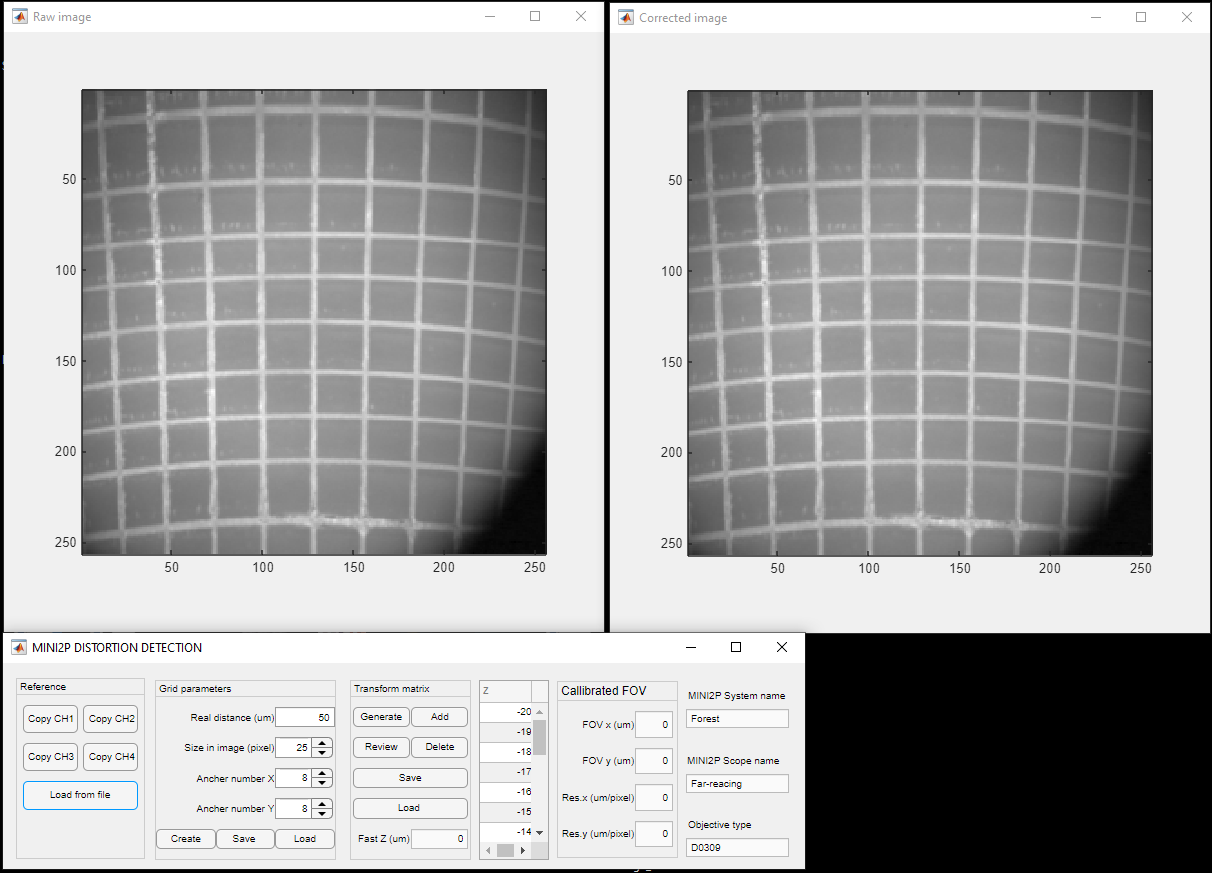
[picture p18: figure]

3 Generate anchor points: Under “Grid parameters” the anchor points properties can be adjusted. The “Real distance” should reflect the distance between the intersection points of the actual grid sample (i.e. 50 μm). Adjust “Anchor number X” and “Anchor number Y” such that approximately each intersection point in your image has an anchor point (the blue dots below) corresponding to it. Subsequently, you will manually drag the blue dots using your cursor to the corresponding intersection points in the Raw image. The transform matrix will then result in the intersection point being positioned at the place where the anchor point originally was (i.e. in an even, orthogonal grid pattern). “Size in image (pixel)” should be optimized such that you are not dragging points outwards, as this will result in the edges of the corrected image having NaN pixels. However, you do not want to be dragging points inwards more than what is strictly necessary either.

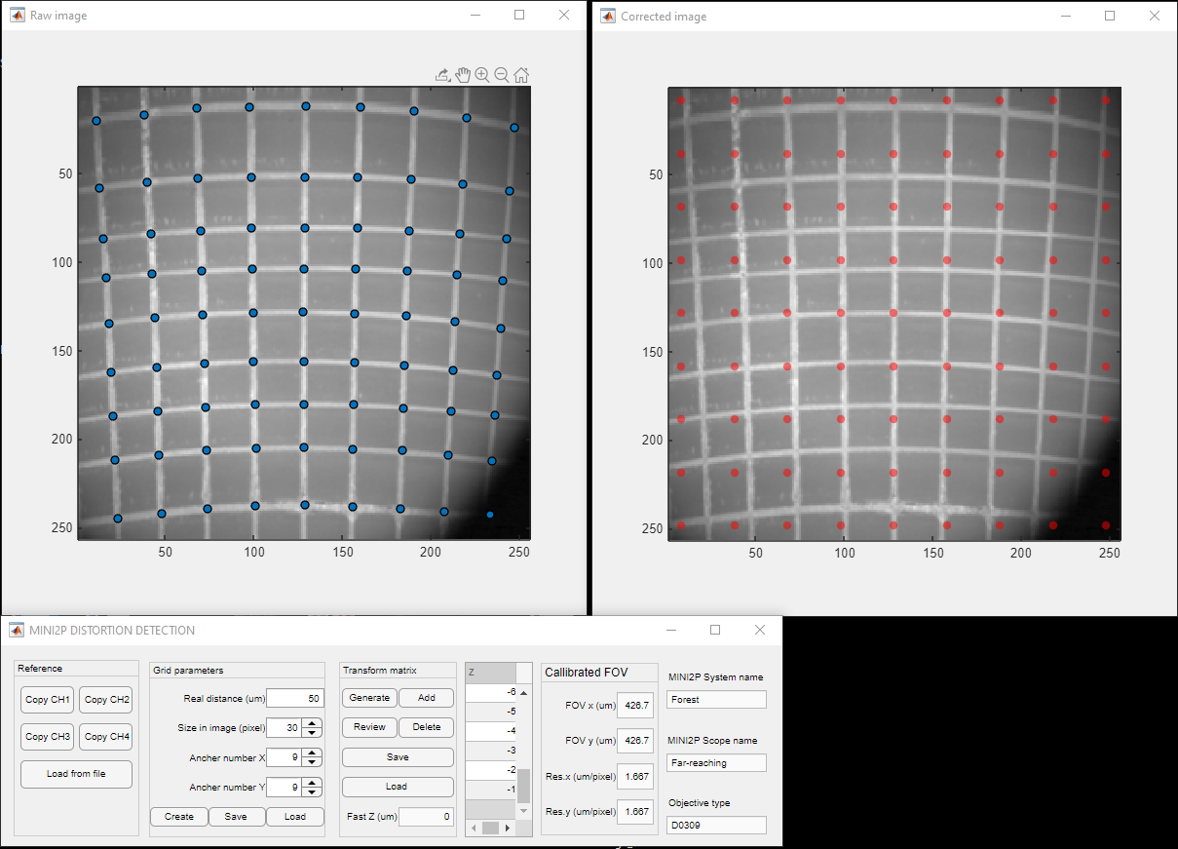
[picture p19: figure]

4 Preview the correction results: Once you are starting to become happy with how you have positioned your anchor points, the corrected image can be previewed by pressing “Generate” under “Transform matrix”. The positions of the anchor points should be further adjusted until the “Corrected image” shows an even and orthogonal grid pattern. Once you are happy with the result, press “Add”.

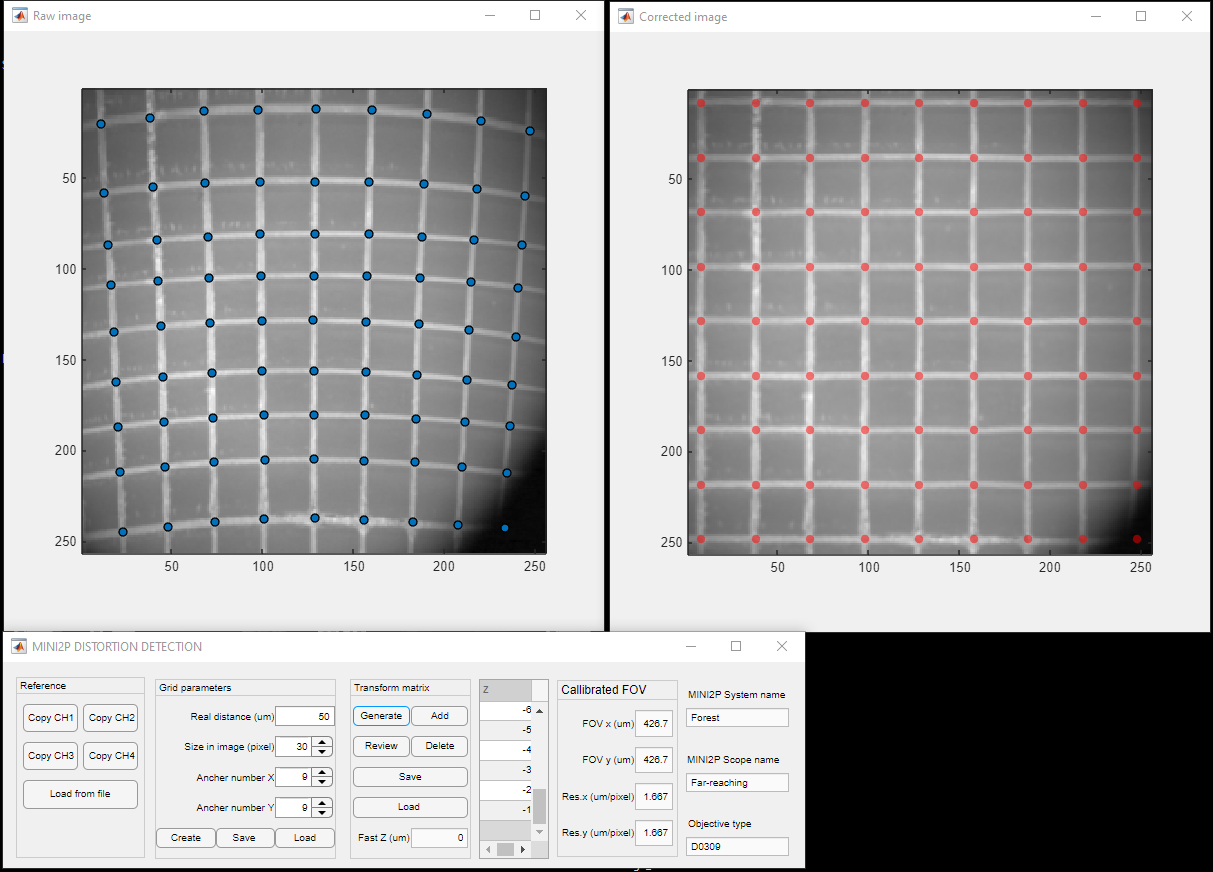
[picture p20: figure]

5 Output the anchor points (optional): The (adjusted and dragged) anchor points can be saved as a .mat table by pressing “Save” under “Grid parameters”. These points can then be applied to future images by pressing “Load” and selecting the desired .mat file.

6 Change focal plane with fastZ and redo the distortion measument: The distortion will typically change slightly at different focal planes and it can therefore be smart to generate new transform matrices at several depths (for instance for every 10 or 20 um). The easiest way to do this is probably to load the anchor points created at Fast Z (um) = 0 for the other depths and then adjust them slightly so that they perfectly fit the images captured at these other focal planes. For every depth you adjust the anchor points at and are happy with the result, click “Add” under “Transform matrix” to save the transformation. When imaging at later instances the transformation created at the focal plane closest to your current image plane will be applied.

7 Output the Transformation Matrix: When you have done the adjustment and added the results at all desired focal planes, the final 3D transformation matrix can be saved. To do this press “Save” under “Transform matrix”. This will result in a .mat table which can then be applied to your imaging data in the future to correct for distortion.

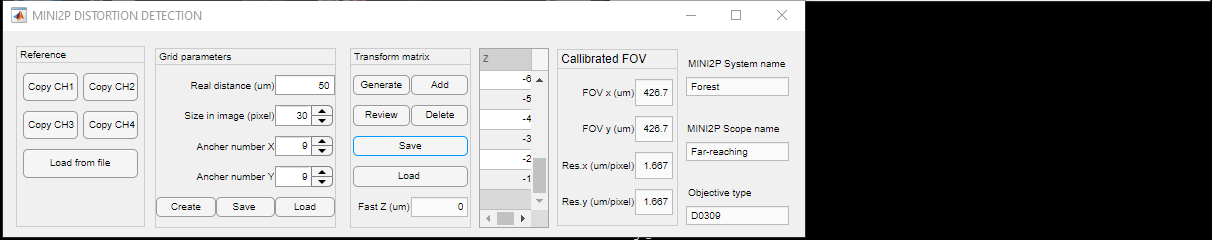
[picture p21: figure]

Note! Once you “Generate” a transform matrix the values under “Calibrated FOV” will be filled in. These are identified based on that the distance between two anchor points is known to be 50 um. Based on this data the corrected imaging data from future session will therefore also have accurate um/pixel and FOV values which can be useful during analysis.

8 Register the Transformation matrix in MINI2P device: As long as you saved the Transformation Matrix somewhere. Now you need to register it in MINI2P. In future, the Transformation matrix will be automatically load in SI when do distortion correction.

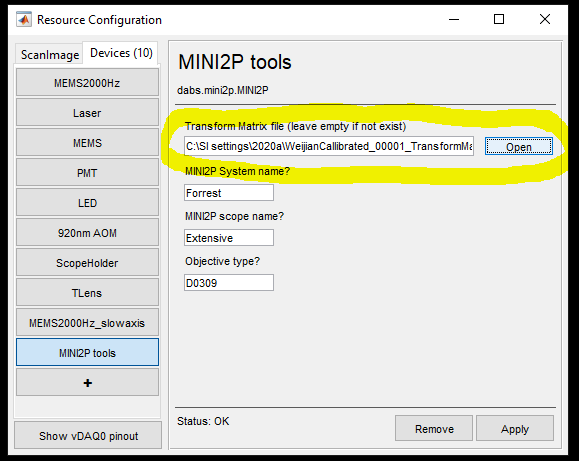
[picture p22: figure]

Note! The safest place to save and load the transform matrix is the same folder you safe the SI MDF and user settings. Do not recommend to safe the transform matrix in network disk or folder that need administrator right.

2. Distortion Correction.

Summary:

This function will do the distortion correction on selected data by using the pre-selected transformation matrix (generated by the function “Distortion Detection” described above). It uses the transformation matrix registered in MINI2P device page. It detects the focal plane in which the raw data was recorded automatically and then use the calibration that was generated with the nearest Z position to do the correction.

It saves the corrected image in the same folder as the raw data folder that the user selected. The SI tiff header is maintained in the corrected data as in the raw data, adding a tag (structure SI.Custom in SI tiff header) indicating which transformation matrix was used, and the MINI2P related information (MINI2P system name, miniscope name, and the objective type). How to find this information was descripted below.

Note! This function will do the correction to all raw tiff files generated by SI in the folder user selects. If any of the tiff files was corrected before (has tag SI.Custom in tiff header), this function will give a warning, and skip this file. If it detects that the zoom factor in the data to correct is different from the zoom used to generate the transform matrix, it gives a warning too. But the user can choose to continue the correction or skip this data and jump to the next.

Output definition:

1. Grid parameters for anchoring points.

2. Calibrated transformation matrix.

This file will be generated when you press “save” in the panel “Transform Matrix” of “MINI2P DISTORTION DETECTION”. It includes the transformation matrix and related information in each focal plane you added into the look up table. Here is a snapshot of the content in each plane:

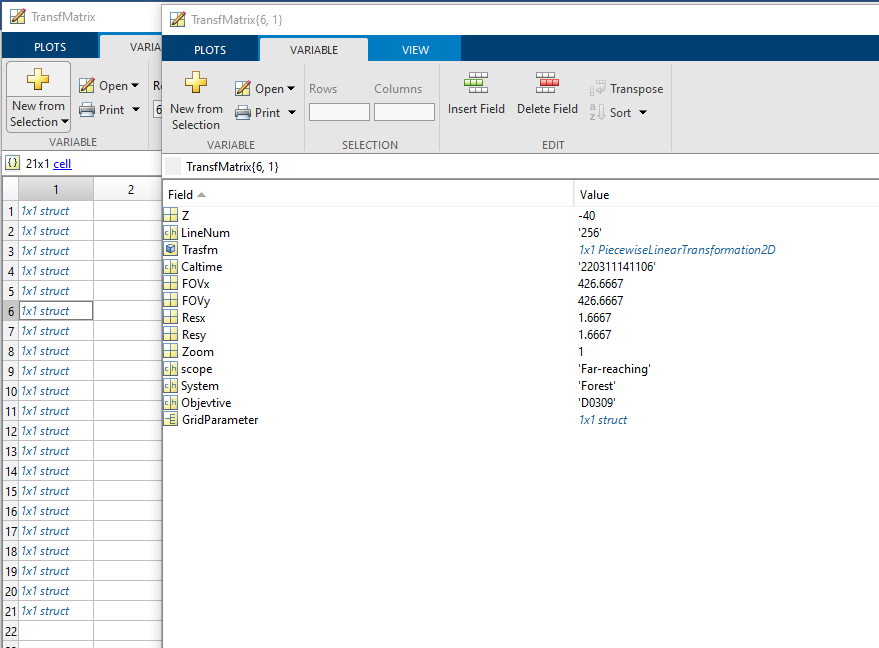
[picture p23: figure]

This figure shows how each cell (calibration in one fast-z position) in the transformation matrix file (cell array) looks like.

3 Distortion corrected data.

The corrected data will be saved in the same file as the raw data, with a name extension of: raw file name_distcorrected,tiff. The corrected data has the tiff header that SI saved, and can be reloaded into SI for alignment, motion correction, or other purpose. The tiff header also contains additional custom information and distortion correction information (see below).

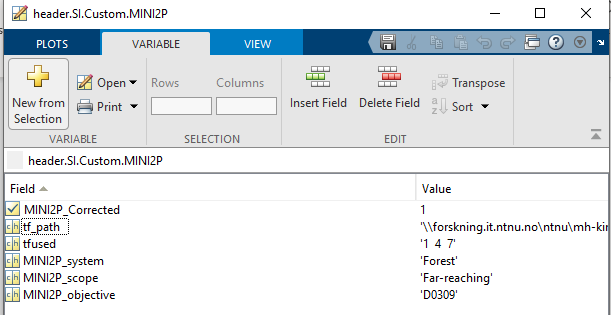
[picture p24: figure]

Readout of custom MIN2P information from the SI tiff header of corrected data.

5 Transformation matrix related information

i) Transformation matrix file path

This tells you which transformation matrix file was used to do the correction. This information can be found in two places:

a. MDF.

This figure shows where in MDF you can find the transformation matrix file path

b. SI tiff header of the corrected the correction data. To access this data, use SI function:

[header, Aout, imgInfo] = scanimage.util. opentif (filename);

Transformation matrix path: header.SI.Custom.MINI2P.tf_path;

ii) Transformation matrix ID used in each data.

This tells you which matrix in the transformation matrix file (cell array) was used to do the correction. It was decided by searching for the matrix that was calibrated in the fast-z position with shortest distance to the fast-z position where the raw date was recorded from. If multiplane imaging was applied, it indicates one number for each plane. The transformation matrix ID is saved in the SI tiff header during correction data generation. To access this information, use SI function:

[header, Aout, imgInfo] = scanimage.util. opentif (filename);

Transformation used for the data: header.SI.Custom. MINI2P.tfused.


This figure shows the custom information in SI tiff header of one corrected data file (3-plane recording). Here, number 1, 4 and 7 matrixes in the transformation matrix file were used to do the correction for each plane, respectively.

5 MINI2P related information (MINI2P system name, miniscope name, and the objective type).

This information can be found in three places:

i. Machine data file of SI:

ii. Transformation matrix saved during “Distortion Detection”;


iii. Tiff header of the distortion corrected image:

[header, Aout, imgInfo] = scanimage.util. opentif (filename);

System name: header.SI.Custom. MINI2P.MINI2P_system.

Scope name: header.SI.Custom. MINI2P.MINI2P_scope.

Objective name: header.SI.Custom. MINI2P.MINI2P_objective.


Note: the field of “Custom” only appear after the distortion correction (not exist in raw data).

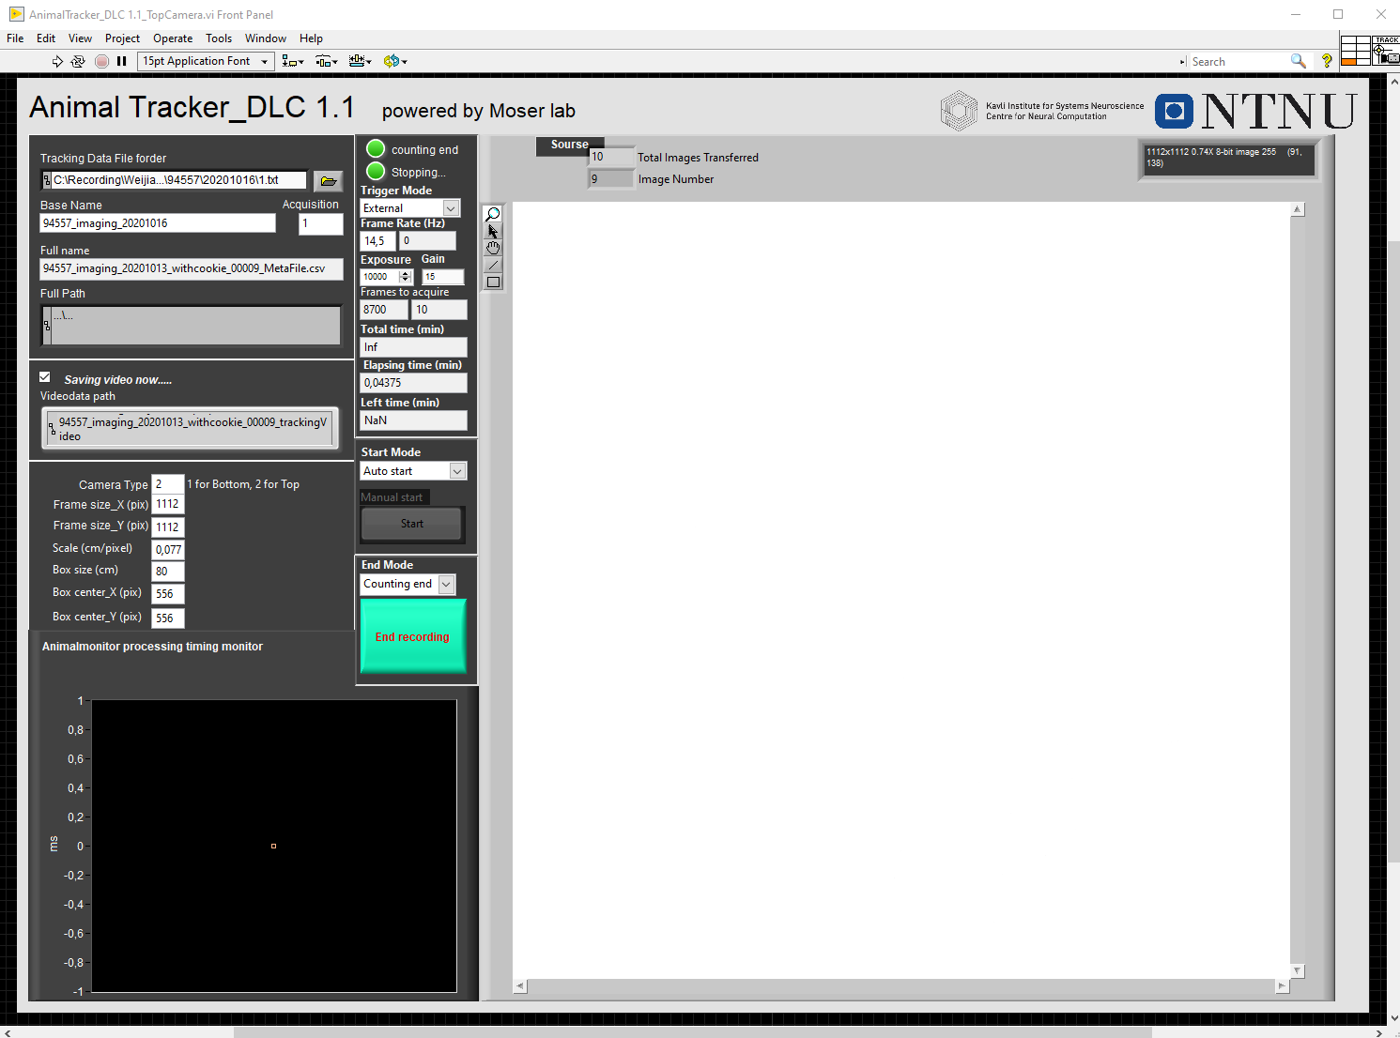
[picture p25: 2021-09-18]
Software/AnimalTracker/AnimalTracker-overview.png

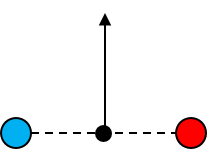
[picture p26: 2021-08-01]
Analysis/Applications/NATEX/pic/DLC2_head.png

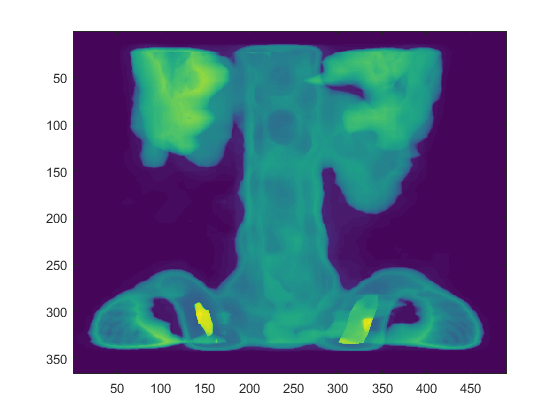
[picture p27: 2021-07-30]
Analysis/+CMP_WJ/html/matplotlib_doc_02.png

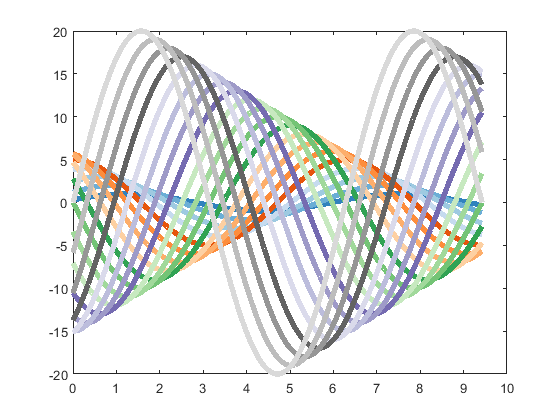
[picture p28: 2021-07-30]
Analysis/+CMP_WJ/html/matplotlib_doc_11.png

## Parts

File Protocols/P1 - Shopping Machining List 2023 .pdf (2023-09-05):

## P1– Shopping & Machining List

Item
ID
Source | Accessibility | Name/Description
(Material for self-made)
Link | Image | Quantity

## General tools

a. | Thorlabs | purchase | Spanner wrench 1 | SPW30 (https://www.thorlabs.com/thorproduct.cfm?partnumber=SPW603) | 1
b. | Thorlabs | purchase | Fiber stripping tool | FTS4 (https://www.thorlabs.com/thorproduct.cfm?partnumber=FTS4) | 1
c. | Thorlabs | purchase | Fiber cleaver | XL411 (https://www.thorlabs.com/thorproduct.cfm?partnumber=XL411) | 1
d. | Thorlabs | purchase | Spanner wrench 2 | SPW602 (https://www.thorlabs.com/thorproduct.cfm?partnumber=SPW602) | 1
e. | Thorlabs | purchase | UV Curing LED system | CD20K2 (https://www.thorlabs.com/thorproduct.cfm?partnumber=CS20K2) | 1
f. | Thorlabs | purchase | Handheld laser source (635nm) Single mode patch cable | HLS635 (https://www.thorlabs.com/thorproduct.cfm?partnumber=HLS635) P1-630Y-FC-2 (https://www.thorlabs.com/thorproduct.cfm?partnumber=P1-630Y-FC-2) | 1 1
g. | Thorlabs | purchase | Power and energy meter Photodiode power sensor | PM100D (https://www.thorlabs.com/thorproduct.cfm?partnumber=PM100D) S121C (https://www.thorlabs.com/thorproduct.cfm?partnumber=S121C) | 1 1

h. | Thorlabs | purchase | Green LED (530nm) T-Cube LED Driver Power supply | M530F2 (https://www.thorlabs.com/thorproduct.cfm?partnumber=M530F2) LEDD1B (https://www.thorlabs.com/thorproduct.cfm?partnumber=LEDD1B) KPS201 (https://www.thorlabs.de/thorproduct.cfm?partnumber=KPS201) | 1 1 1
i. | Thorlabs | purchase | NIR detector card | VRC4 (https://www.thorlabs.com/thorproduct.cfm?partnumber=VRC4) | 1
j. | Thorlabs | purchase | Lens cleaning tissues | MC-5 (https://www.thorlabs.com/thorproduct.cfm?partnumber=MC-5) | 1
k. | RS | purchase | Foam cotton bud & swabs | Swabs (https://no.rs-online.com/web/p/cotton-buds/4077931) | 1
l. | Thorlabs | purchase | Optical adhesive | NOA61 (https://www.thorlabs.com/thorproduct.cfm?partnumber=NOA61) | 1
m. | Thorlabs | purchase | Splice protector sleeve | SPS60 (https://www.thorlabs.com/thorproduct.cfm?partnumber=SPS60) | 1-2
n. | Thorlabs | purchase | Distortion grid with 50um grid spacing Fluorescent marker | R1L3S3P (https://www.thorlabs.de/thorproduct.cfm?partnumber=R1L3S3P) - | 1 1
o. | Winjee | purchase | Silicone rubber back glue | 704 (https://www.amazon.co.uk/WINJEE-Silicone-Industrial-Adhesive-Rubber/dp/B07WBZBYY5) | 1
p. 3M | Loctite | purchase | Epoxy (black) Super glue | DP420 (https://www.3m.co.uk/3M/en_GB/p/d/b40066431/) 415 (https://www.henkel-adhesives.com/us/en/product/instant-adhesives/loctite_415.html) | 1 1

q. | Ahlsell | purchase | Heat gun | link (https://www.ahlsell.no/33/verktoy/elektriske-handverktoy-og-maskiner/elektriske-handverktoy-nettilkoblet/varmluftpistoler/8805144-f63a2a60/) | 1
r. | APE | purchase | Pulsed Check autocorrelator | APE-NX (https://www.ape-berlin.de/en/autocorrelator/pulsecheck/) | 1
s. | Thorlabs | purchase | Base to fixate Pulse Check on Optical Breadboard | MB2025/M (https://www.thorlabs.com/thorProduct.cfm?partNumber=MB2025/M) | 1
t. | Fabory | purchase | M2x5H Philips 7985225 | M2screws (https://www.fabory.com/en/cross-recessed-raised-cheese-head-screw-phillips-din-7985-h-stainless-steel-a2-m2x5/p/51340020005) | >10
u. | TRfastenings | purchase | M3x3mm Pan Head PoziDriv Machine Screw DIN7985 | M3x3 (https://www.trfastenings.com/products/Catalogue/Screws-and-Bolts/Machine-Screws/Pan-Head/PoziDriv) | >3
v. | Thorlabs | purchase | M4 capscrews kit | HW-KIT1/M (https://www.thorlabs.com/thorProduct.cfm?partNumber=HW-KIT1/M) | 1
w. | Elfa Distrelec | purchase | Air duster Green PRF | PRF 4-44 (https://www.elfadistrelec.no/en/compressed-air-spray-405-ml-prf-prf-green-trigger-44-nfl-405ml/p/30098436?q=&pos=2&origPos=2&origPageSize=50&track=true) | 1
x. Surface | Solutions | purchase | Black rubber spray | SS black (https://www.paintshop.no/home/303-blouse.html) | 1
y. | Elfa Distrelec | purchase | Tweezers Carbon Fibre Forceps | 301-51-451 (https://www.elfa.se/en/tweezer-carbon-fibre-flat-squared-straight-130mm-ideal-tek-279cfr-sa/p/30151451) 11270-20 (https://www.finescience.com/en-US/Products/Forceps-Hemostats/Dumont-Forceps/Dumont-7b-Forceps/11270-20) | 1 1

## Core optics module

### Mechanical components

1 | Thorlabs | purchase | Nexus breadboard | B3045L (https://www.thorlabs.com/thorproduct.cfm?partnumber=B3045L) | 1

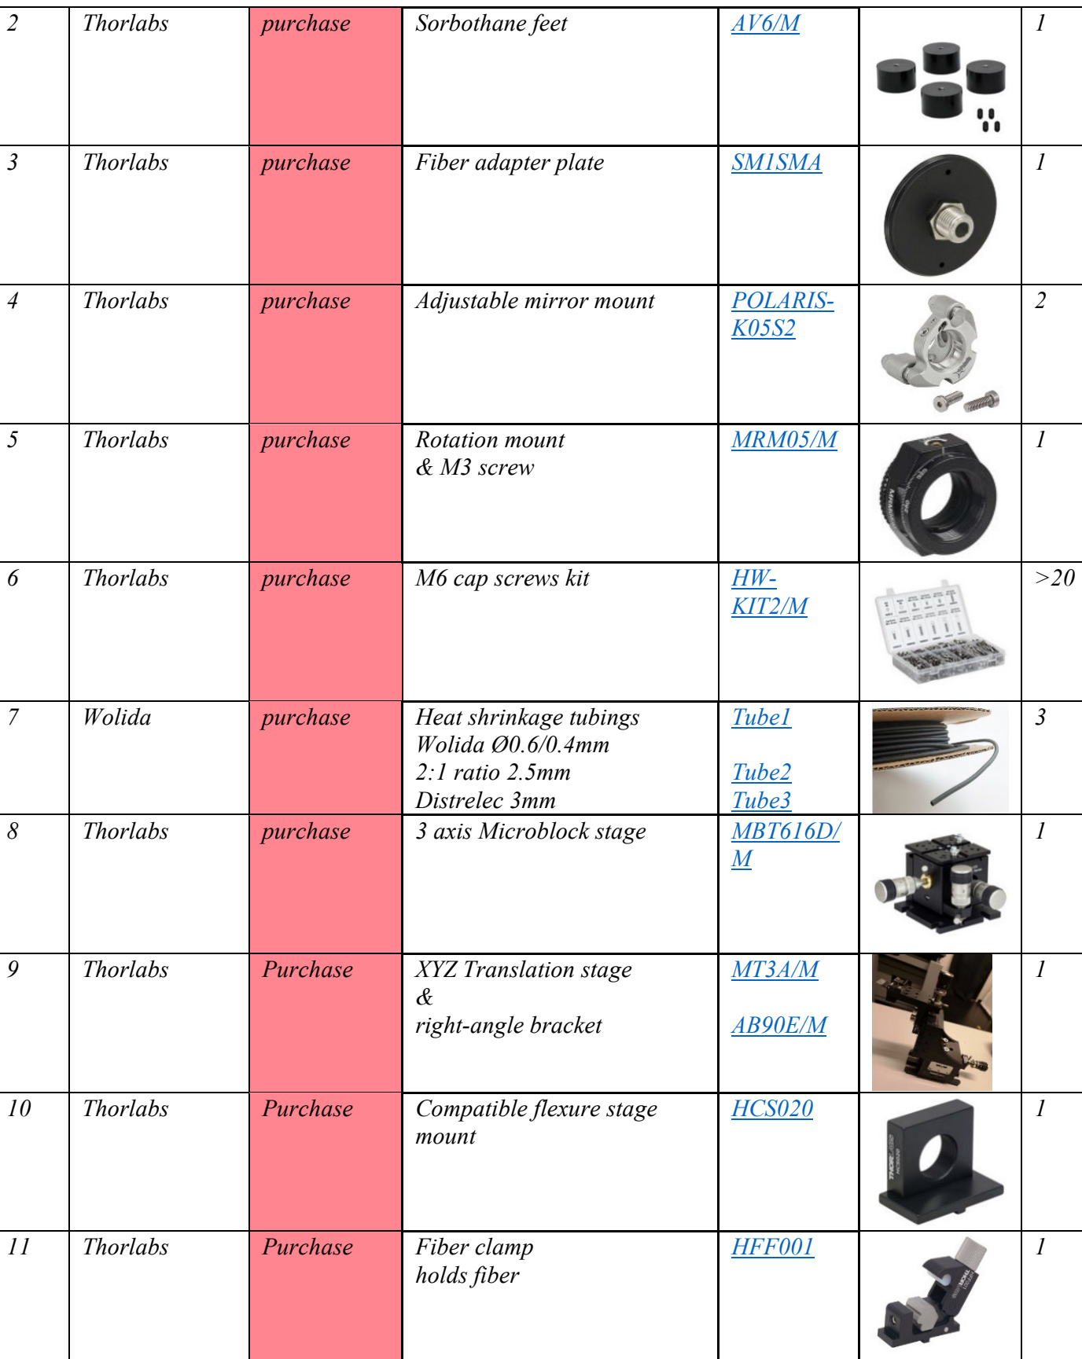
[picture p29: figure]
Thorlabs; purchase; Sorbothane feet; AV6/M (https://www.thorlabs.com/thorproduct.cfm?partnumber=AV6/M); Fiber adapter plate; SM1SMA (https://www.thorlabs.com/thorproduct.cfm?partnumber=SM1SMA#ad-image-0); Adjustable mirror mount; POLARIS-K05S2 (https://www.thorlabs.com/thorproduct.cfm?partnumber=POLARIS-K05S2); Rotation mount & M3 screw; MRM05/M (https://www.thorlabs.com/thorproduct.cfm?partnumber=MRM05/M); M6 cap screws kit; HW-KIT2/M (https://www.thorlabs.com/thorproduct.cfm?partnumber=HW-KIT2/M); 3 axis Microblock stage; MBT616D/ M (https://www.thorlabs.com/thorproduct.cfm?partnumber=MBT616D#ad-image-0); Purchase; Compatible flexure stage mount; HCS020 (https://www.thorlabs.com/thorproduct.cfm?partnumber=HCS020)

7 | Wolida | purchase | Heat shrinkage tubings Wolida Ø0.6/0.4mm 2:1 ratio 2.5mm Distrelec 3mm | Tube1 (https://m.alibaba.com/product/60562691813/WOLIDA-heat-shrinkable-tube-black-flame.html) Tube2 (https://www.amazon.com/100FT-BLACK-HEAT-SHRINK-TUBING/dp/B006HU7XCA) Tube3 (https://www.distrelec.biz/en/heat-shrink-tubing-3mm-black-polyolefin-10m-hellermanntyton-his-bk/p/15505468) | 3
9 | Thorlabs | Purchase | XYZ Translation stage & right-angle bracket | MT3A/M (https://www.thorlabs.de/thorproduct.cfm?partnumber=MT3A/M) AB90E/M (https://www.thorlabs.com/thorproduct.cfm?partnumber=AB90E/M#ad-image-0) | 1
11 | Thorlabs | Purchase | Fiber clamp holds fiber Bare fiber adapter &Flat base to glue into (e.g.) | HFF001 (https://www.thorlabs.com/thorproduct.cfm?partnumber=HFF001) S140-BFA (https://www.thorlabs.com/thorproduct.cfm?partnumber=S140-BFA) XT95P3 (https://www.thorlabs.de/thorProduct.cfm?partNumber=XT95P3) | 1 3 1

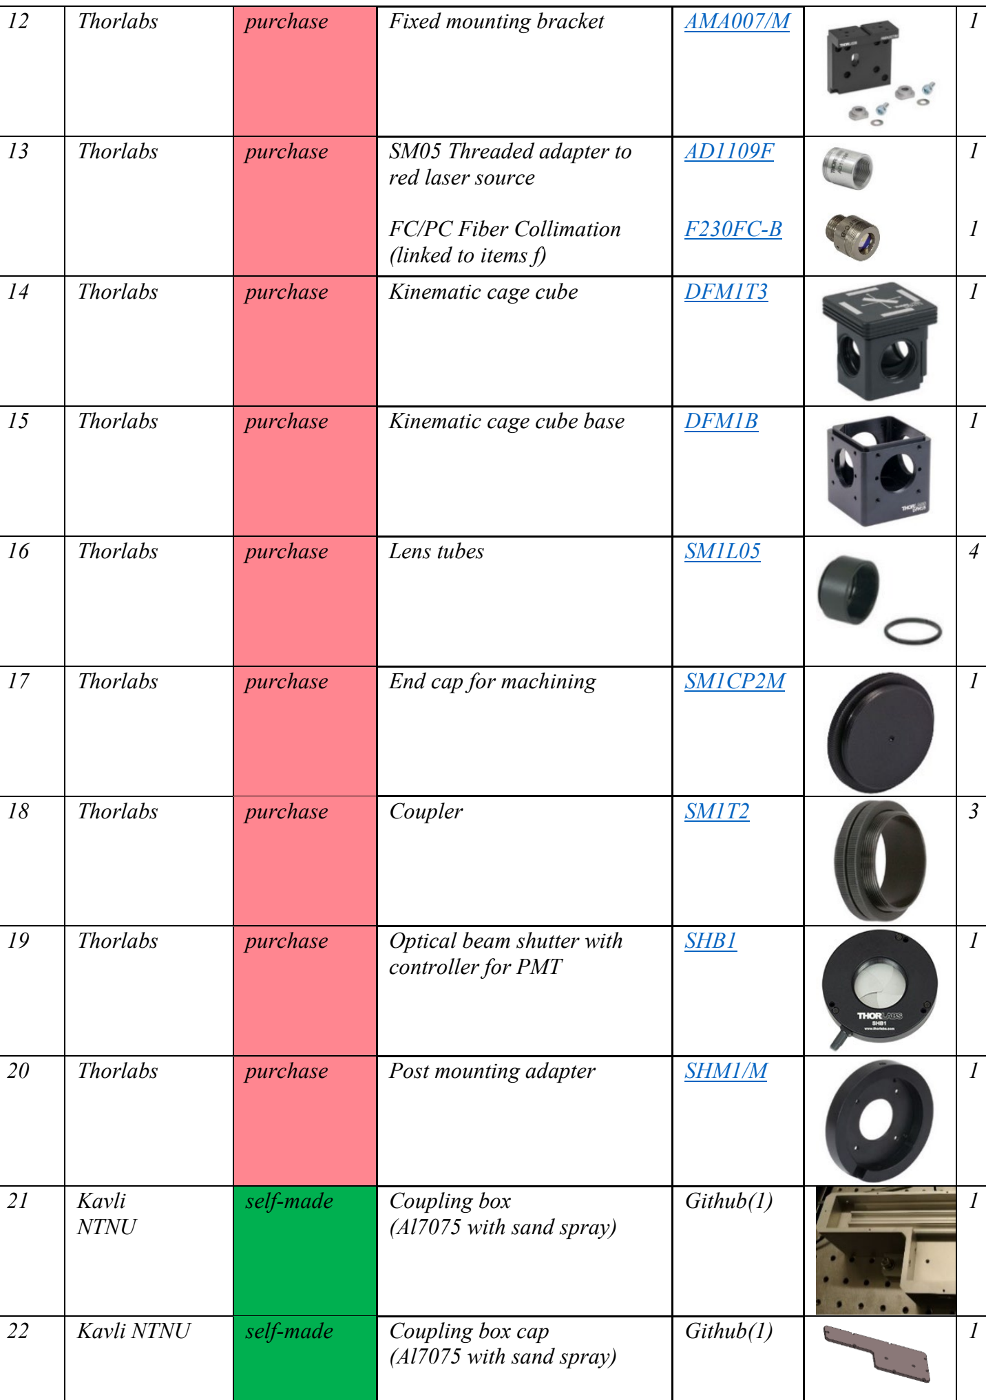
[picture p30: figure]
Thorlabs; purchase; Fixed mounting bracket; AMA007/M (https://www.thorlabs.com/thorproduct.cfm?partnumber=AMA007/M); Kinematic cage cube; DFM1T3 (https://www.thorlabs.de/thorproduct.cfm?partnumber=DFM1T3); Kinematic cage cube base; DFM1B (https://www.thorlabs.com/thorproduct.cfm?partnumber=DFM1B/M); Lens tubes; SM1L05 (https://www.thorlabs.com/thorproduct.cfm?partnumber=SM1L05); End cap for machining; SM1CP2M (https://www.thorlabs.com/thorproduct.cfm?partnumber=SM1CP2M); Coupler; SM1T2 (https://www.thorlabs.com/thorproduct.cfm?partnumber=SM1T2); Post mounting adapter; SHM1/M (https://www.thorlabs.com/thorproduct.cfm?partnumber=SHM1/M)

13 | Thorlabs | purchase | SM05 Threaded adapter to red laser source FC/PC Fiber Collimation (linked to items f) | AD1109F (https://www.thorlabs.com/thorproduct.cfm?partnumber=AD1109F) F230FC-B (https://www.thorlabs.com/thorProduct.cfm?partNumber=F230FC-B) | 1 1
19 | Thorlabs | purchase | Optical beam shutter with controller for PMT | SHB1 (https://www.thorlabs.com/thorproduct.cfm?partnumber=SHB1#ad-image-0) | 1
21 | Kavli NTNU | self-made | Coupling box (Al7075 with sand spray) | Github(1) | 1
22 | Kavli NTNU | self-made | Coupling box cap (Al7075 with sand spray) | Github(1) | 1

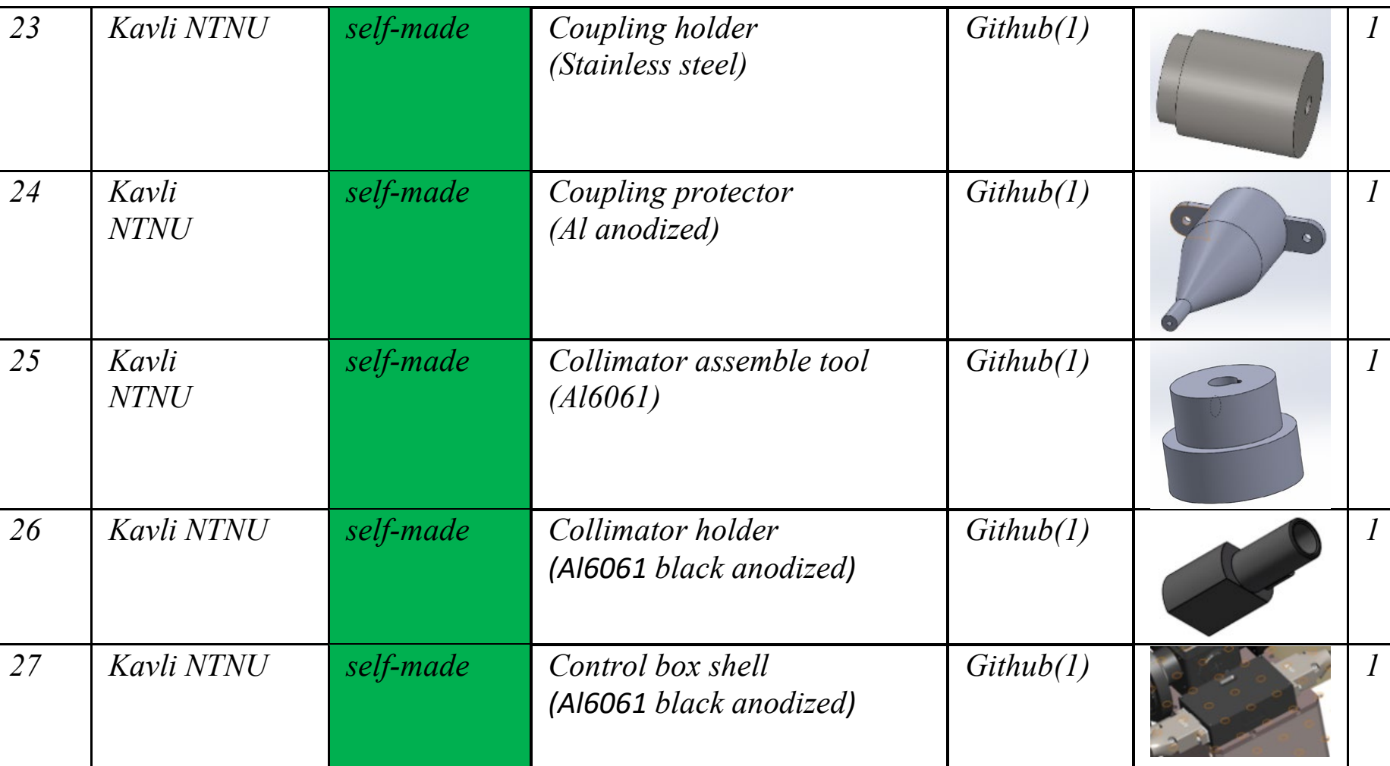
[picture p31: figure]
Kavli NTNU; self-made; Coupling holder (Stainless steel); Github(1); Coupling protector (Al anodized); Collimator assemble tool (Al6061); Collimator holder (Al6061 black anodized)

27 | Kavli NTNU | self-made | Control box shell (Al6061 black anodized) | Github(1) | 1
28 | Kavli NTNU | self-made | Control box cap (Al6061 black anodized) | Github(1) | 1

### Optical components

29 | Femtosecond laser with center wavelength at 920nm, 80MHz, pulse width 100-130fs, and average power >1W Example suppliers: TOPTICA, SPARKLASER, COHERENT | purchase | Laser source Spark Laser offers higher positive GDD (up to 120 000 fs² ) | Example types: FemtoFibe r ultra 920 (https://www.toptica.com/products/psfs-fiber-lasers/femtofiber-ultra/femtofiber-ultra-920/) ALCOR 920 X-Sight (https://spark-lasers.com/wp-content/uploads/2022/10/Specs_sheet_ALCOR_09-2022-B.pdf) | 1 OR 1
30 | LabMaker | modify | Tapered fiber bundle (TFB) XMLG, Ø.027”x98.4”[2.5 m] Drawing C54706.04 PRODUCTION DISCONTINUED! Grin Fiber Bundle (GFB) New solution! with items: 30.1 Fiber Bundle by SCHOTT Part Number 1840314 Drawing C54706.1X | 1838003 (https://www.schott.com/products/flexible-light-guides) 1840314 | 1

| 30.2 AR windows by Sunlight (dia1.8x0.2mm,S1:HT T>99%@450-700nm, AOI=0deg) 30.3 GRIN lens #64-520 Or #64-526 (1.8mm Dia, 670nm DWL, 0.23mm WD) 30.4 GFB holder Note: GFB is compatible with version2 of Scopebody P3 (see item #104_2023) | WIN1.8x0. 2-S1AR450-700 #64-520 (https://www.edmundoptics.com/p/18mm-dia-670nm-dwl-023mm-wd-uncoated-grin-lens/19232/) Or #64-526 (https://www.edmundoptics.eu/p/18mm-dia-810nm-dwl-023mm-wd-uncoated-grin-lens/19238/) GitHub (https://github.com/kavli-ntnu/MINI2P_toolbox/tree/main/Hardware/GFB)

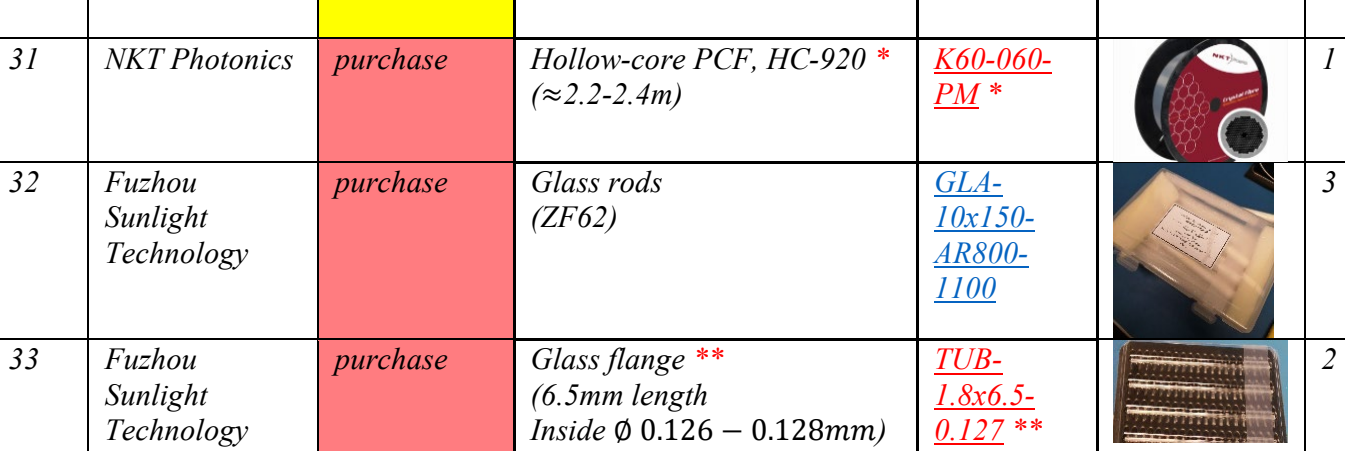
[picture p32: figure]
NKT Photonics; purchase; (≈2.2-2.4m) Hollow-core PCF, HC-920 *; K60-060-PM (https://www.nktphotonics.com/lasers-fibers/product/hollow-core-photonic-crystal-fibers/) *; Fuzhou Sunlight Technology; Glass rods (ZF62); GLA-10x150-AR800-1100 (http://sunlight-tec.com/en/cpzx.asp)

33 | Fuzhou Sunlight Technology | purchase | Inside ∅ 0.126 − 0.128mmmm) Glass flange ** (6.5mm length | TUB-1.8x6.5-0.127 (http://sunlight-tec.com/en/cpzx.asp) ** | 2

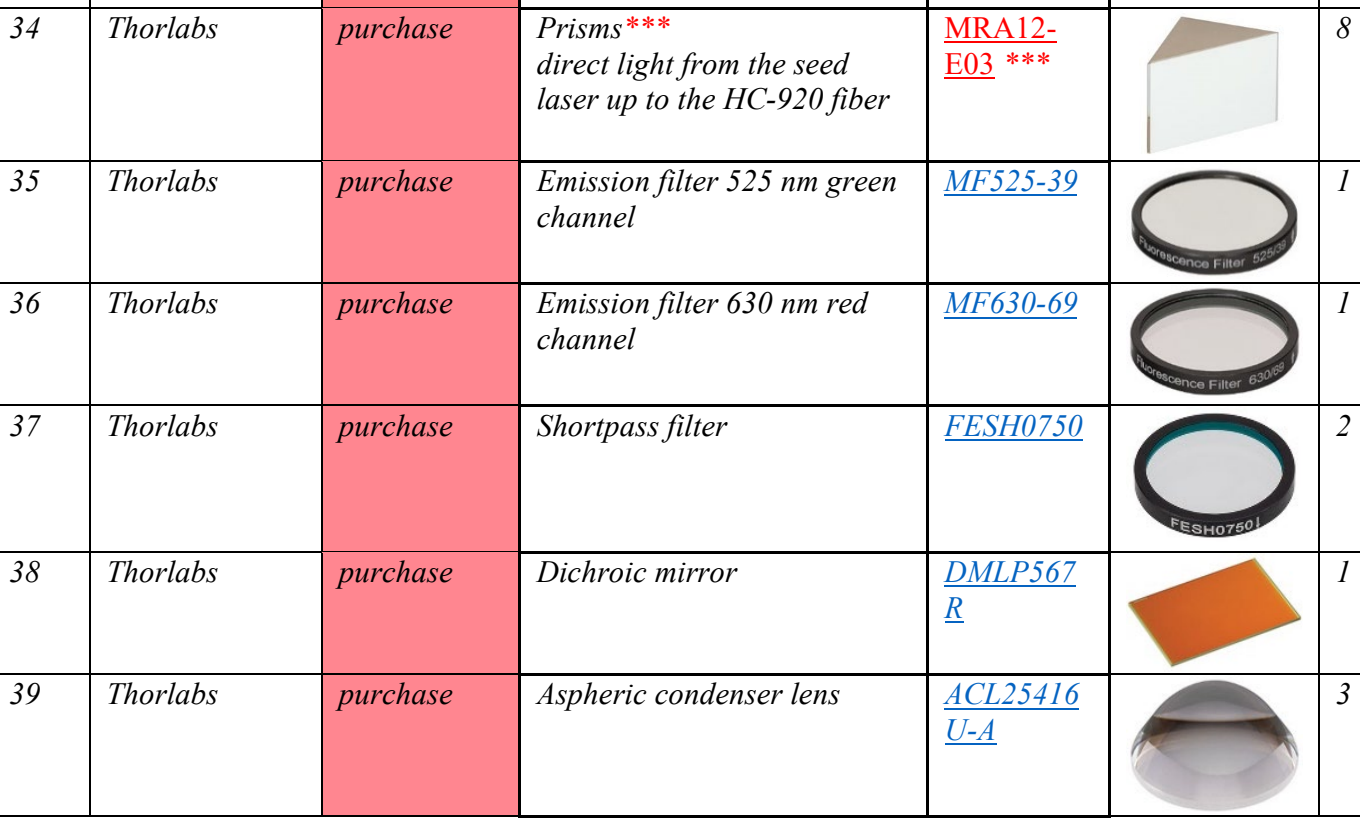
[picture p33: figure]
Thorlabs; purchase; Shortpass filter; FESH0750 (https://www.thorlabs.com/thorproduct.cfm?partnumber=FESH0750); Dichroic mirror; DMLP567 R (https://www.thorlabs.com/thorproduct.cfm?partnumber=DMLP567R); Aspheric condenser lens; ACL25416 U-A (https://www.thorlabs.com/thorproduct.cfm?partnumber=ACL25416U-A)

34 | Thorlabs | purchase | Prisms*** direct light from the seed laser up to the HC-920 fiber | MRA12-E03 (https://www.thorlabs.com/thorProduct.cfm?partNumber=MRA10-E03) *** | 8
35 | Thorlabs | purchase | Emission filter 525 nm green channel | MF525-39 (https://www.thorlabs.com/thorproduct.cfm?partnumber=MF525-39) | 1
36 | Thorlabs | purchase | Emission filter 630 nm red channel | MF630-69 (https://www.thorlabs.com/thorproduct.cfm?partnumber=MF630-69) | 1

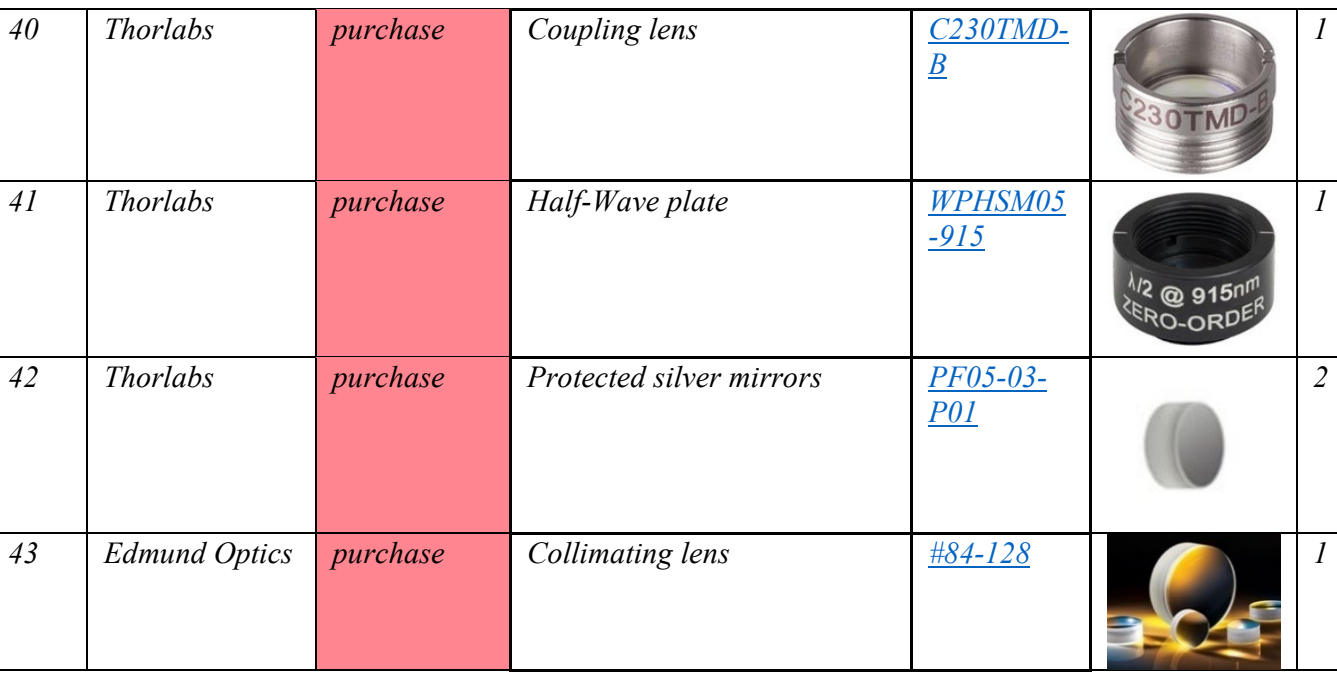
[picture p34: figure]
Thorlabs; purchase; Coupling lens; C230TMD-B (https://www.thorlabs.com/thorproduct.cfm?partnumber=C230TMD-B); Half-Wave plate; WPHSM05 -915 (https://www.thorlabs.com/thorproduct.cfm?partnumber=WPHSM05-915); Protected silver mirrors; PF05-03-P01 (https://www.thorlabs.com/thorproduct.cfm?partnumber=PF05-03-P01); Edmund Optics; Collimating lens; #84-128 (https://www.edmundoptics.com/p/2mm-dia-x-4mm-fl-vis-nir-coated-achromatic-lens/27236/)

### Electrical components

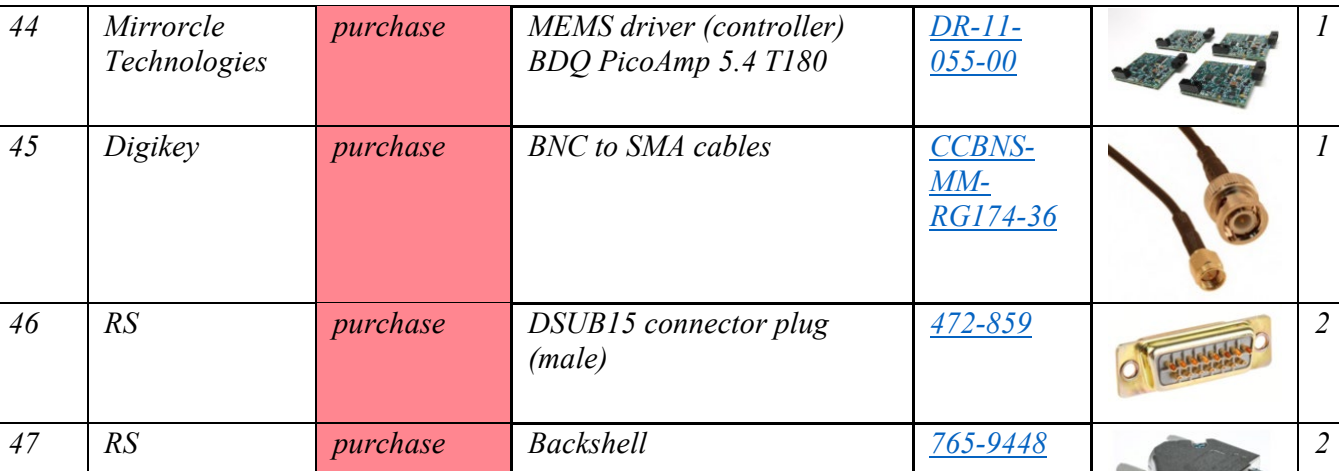
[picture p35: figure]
Digikey; purchase; BNC to SMA cables; CCBNS-MM-RG174-36 (https://www.digikey.no/product-detail/no/crystek-corporation/CCBNS-MM-RG174-36/744-1249-ND/1767703); DSUB15 connector plug (male); 472-859 (https://no.rs-online.com/web/p/d-sub-connectors/0472859/); Backshell; 765-9448 (https://no.rs-online.com/web/p/d-sub-connectors/7659448)

44 | Mirrorcle Technologies | purchase | MEMS driver (controller) BDQ PicoAmp 5.4 T180 | DR-11-055-00 (https://www.mirrorcletech.com/wp/products/hardware/drivers/analog/) | 1

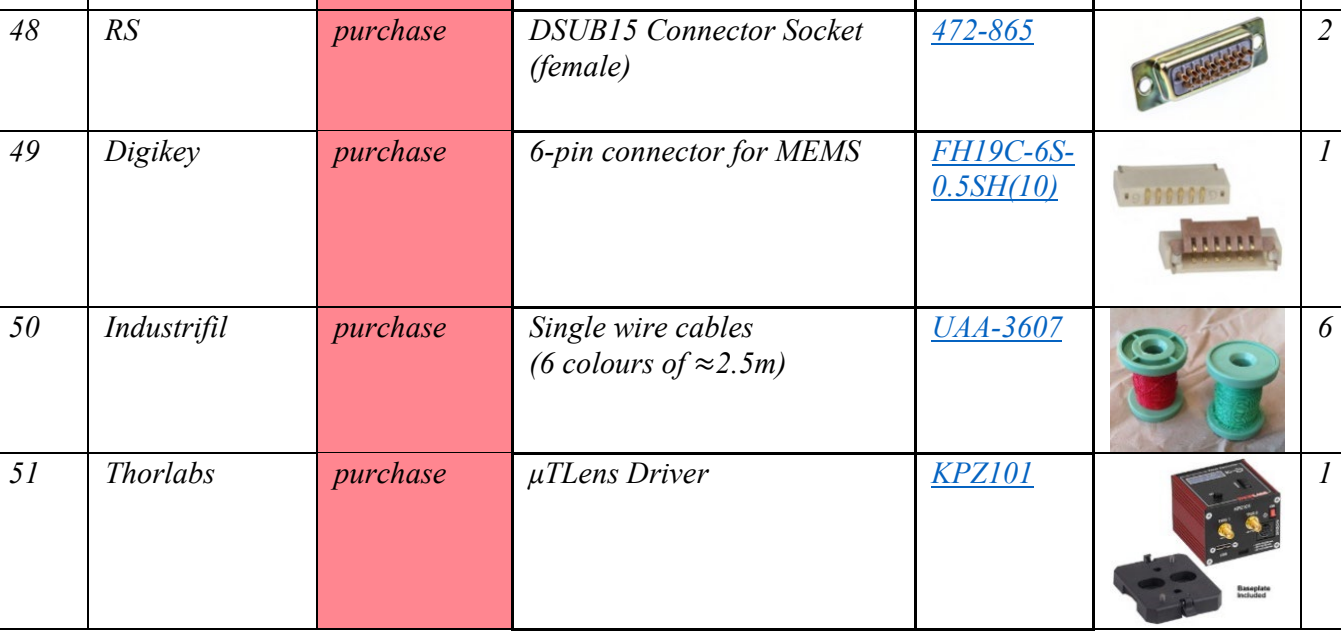
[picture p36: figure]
purchase; DSUB15 Connector Socket (female); 472-865 (https://no.rs-online.com/web/p/d-sub-connectors/0472865/); Digikey; 6-pin connector for MEMS; FH19C-6S-0.5SH(10) (https://www.digikey.no/product-detail/no/hirose-electric-co-ltd/FH19C-6S-0-5SH-10/H125824CT-ND/9360234); Thorlabs; μTLens Driver; KPZ101 (https://www.thorlabs.com/thorproduct.cfm?partnumber=KPZ101)

50 | Industrifil | purchase | (6 colours of ≈2.5m) Single wire cables | UAA-3607 (http://www.industrifil.com/insulated.html) | 6

52 | Thorlabs | purchase | PMT | PMT2101/ M (https://www.thorlabs.com/thorproduct.cfm?partnumber=PMT2101/M) | 2
53 | Thorlabs | purchase | Controller for shutter | SHB1 (https://www.thorlabs.de/thorproduct.cfm?partnumber=SHB1#ad-image-0) | 1

## Scope mounting module

### Mechanical components

Thorlabs; purchase; Aluminum optical breadboard; B3060A (https://www.thorlabs.com/thorproduct.cfm?partnumber=B3060A); Sorbothane feet; AV6/M (https://www.thorlabs.de/thorproduct.cfm?partnumber=AV6/M); Precision construction rail L=400mm; XT95B-400 (https://www.thorlabs.com/thorproduct.cfm?partnumber=XT95B-400); Post Mounting Clamp; C1545/M (https://www.thorlabs.com/thorproduct.cfm?partnumber=C1545/M); Manual Rotation Stage; RP03/M (https://www.thorlabs.com/thorproduct.cfm?partnumber=RP03/M); Base for item 58; XT95P3 (https://www.thorlabs.com/thorproduct.cfm?partnumber=XT95P3); Optical post; TR75/M (https://www.thorlabs.com/thorproduct.cfm?partnumber=TR75/M)

56 | Thorlabs | purchase | One-sided construction rail Black Anodized (95x500 mm) | XT95SD-500 (https://www.thorlabs.com/thorproduct.cfm?partnumber=XT95SD-500) | 2
57 | Thorlabs | purchase | Rail carriage suitable for sliding onto item 58 | XT95RC4/ M (https://www.thorlabs.com/thorproduct.cfm?partnumber=XT95RC4/M) | 2

63 | Thorlabs | modify | Running wheel hardboard | Github, TB4 (https://www.thorlabs.com/thorproduct.cfm?partnumber=TB4) | 1/4
64 | Thorlabs | purchase | M6 spacers & washers | W25S050 (https://www.thorlabs.de/thorproduct.cfm?partnumber=W25S050) | >4
65 | Thorlabs | purchase | Spacer on both sides of wheel | PS1M (https://www.thorlabs.com/thorproduct.cfm?partnumber=PS1M) | 2
66 | SKF | purchase | Bearing OD 19mm ID 6mm | 626-2Z (https://no.rs-online.com/web/p/ball-bearings/2867849/) | 1
67 | Thorlabs | purchase | Right-angle clamp | RSA90/M (https://www.thorlabs.de/thorproduct.cfm?partnumber=RSA90/M) | 1
68 | Thorlabs | purchase | Pillar posts | RS50/M (https://www.thorlabs.com/thorproduct.cfm?partnumber=RS50/M) | 2

Thorlabs; purchase; Universal post holder; UPH100/M (https://www.thorlabs.com/thorproduct.cfm?partnumber=UPH100/M#ad-image-0); Adapter camera-lens; SM1A10Z (https://www.thorlabs.com/thorproduct.cfm?partnumber=SM1A10Z); Kavli NTNU; self-made; MINI2P Holder P1 (Al6061); Github(1); MINI2P Holder P2 (Al6061); MINI2P Holder P3 (Stainless steel)

70 | Thorlabs | purchase | Locking Ball and Socket Mount; to support LEDs near Tracking Camera | TRB1/M (https://www.thorlabs.com/thorproduct.cfm?partnumber=TRB1/M) | 8
75 | Kavli NTNU TRfastenings | self-made | MINI2P Holder P4 & screw (Stainless steel) M2.5x5 cap head hexagon socket drive screw, DIN912 | Github(1) M2.5cap (https://www.trfastenings.com/Products/Catalogue/Screws-and-Bolts/Machine-Screws) | 1 1


| | | MINI2P holder P4 version 2 (NEW!) Holder for scope assembly | Github | 1
76 | Kavli NTNU | self-made | Wheel Holder (Stainless steel) | Github | 1
77 | Kavli NTNU TRfastenings | self-made | Headbar holder & screw (Titanium alloy) M3x3mm Pan Head PoziDriv Machine Screw, zinc & clear, DIN7985 | Github M3x3 (https://www.trfastenings.com/Products/Catalogue/Screws-and-Bolts/Machine-Screws/Pan-Head/PoziDriv) | 1 2

### Optical and electrical components

78 | Thorlabs RS | purchase | LED & Accessories 850nm IR LED Array Light Source LED 5m cable Adapter Supply Power for LED | LIU850A (https://www.thorlabs.com/thorproduct.cfm?partnumber=LIU850A) 780-0087 (https://no.rs-online.com/web/p/industrial-automation-cable-assemblies/7800087) 301-29-731 (https://www.elfadistrelec.no/no/koblingsmuffe-1x5-5mm-rett-rnd-connect-rnd-205-00911/p/30129731) 136-1345 (https://no.rs-online.com/web/p/ac-dc-adapters/1361345) | 1 1 1 1


79 | Thorlabs | purchase | Zelux 1.6 MP Monochrome CMOS Camera & adapter SM1 to C-Mount | CS165MU/ M (https://www.thorlabs.com/thorproduct.cfm?partnumber=CS165MU/M) SM1A10Z (https://www.thorlabs.de/thorproduct.cfm?partnumber=SM1A10Z) | 1 1
80 | Edmund Optics | purchase | Lens focal length 4.5mm Or 8.5mm for lateral and frontal camera to control head fixation | 4.5mm (https://www.edmundoptics.com/p/45mm-c-series-fixed-focal-length-lens/29328/) 8.5mm (https://www.edmundoptics.com/p/85mm-f8-23-hpi-series-fixed-focal-length-lens/40682/) | 1
81 | Edmund Optics | purchase | Basler camera for Animal Tracking 16mm EFL Camera Lens Shortpass Filter 875nm | acA2040-90um (https://www.baslerweb.com/en/products/cameras/area-scan-cameras/ace/aca2040-90um/) MVL16M2 3 (https://www.thorlabs.com/thorproduct.cfm?partnumber=MVL16M23) #86-106 (https://www.edmundoptics.com/p/875nm-25mm-diameter-od-4-shortpass-filter/28593/) | 1 1 1

82 Physik
Instrumente
(PI)
purchase | DC Motors | M- 112.2DG (https://www.physikinstrumente.com/en/products/linear-stages/stages-with-stepper-dc-brushless-dc-bldc-motors/m-110-m-111-m-112-compact-linear-stage-412418433/)

3

## Mobile cart and controlling system

### Mechanical and electrical components

83 | Thorlabs | purchase | Mobile cart | POC001 (https://www.thorlabs.com/thorproduct.cfm?partnumber=POC001) | 1
84 | Thorlabs | purchase | Optical breadboard 600x900x55mm | PBG52506 (https://www.thorlabs.com/thorproduct.cfm?partnumber=PBG52506) | 1
85 | Thorlabs | purchase | Optional drawer | POD001 (https://www.thorlabs.com/thorProduct.cfm?partNumber=POD001) | 1
86 | Schroff | purchase | 19-inch rack | Ref 721-2708 (https://no.rs-online.com/web/p/rackmount-cases/7212708/) | 1
87 | McMASTER-CARR | purchase | Span-in nuts | 90680A729 (https://www.mcmaster.com/90680A729/) | 10
88 | Dell | purchase | Workstation is an Intel core i9 with operating windows 10 Pro | 7080 (https://www.dell.com/en-us/work/shop/desktops-all-in-one-pcs/optiplex-7080-tower-and-small-form-factor/spd/optiplex-7080-desktop) | 1
89 | Dell | purchase | (32”to 49”) curved LED-backlit LCD5K2K monitor | Monitor (https://www.dell.com/en-uk/shop/dell-ultrasharp-40-curved-wuhd-monitor-u4021qw/apd/210-ayjf/monitors-monitor-accessories) | 1
90 | Vidrio Technologies LLC | purchase | vDAQ card provides data acquisition and control of Laser, µTLens, shutter, among others | V-vDAQ.R1 (https://vidriotechnologies.com/vdaq/) | 1
91 | Vidrio Technologies LLC | purchase | vDAQ breadboard | V-vDAQ.R1 (https://vidriotechnologies.com/vdaq/) | 1
92 | Physik Instrumente (PI) | purchase | Motion controller for PI motors | C-884.4DC (https://www.physikinstrumente.com/en/products/controllers-and-drivers/motion-controllers-drivers-for-linear-torque-stepper-dc-servo-motors/c-8844dc-c-8846dc-m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) | 1
93 | Femtosecond laser with center wavelength at 920nm, 80MHz, pulse width 100- | purchase | Controller for 920nm laser | Example types: FFUltra92 0 (https://www.toptica.com/products/psfs-fiber-lasers/femtofiber-ultra/femtofiber-ultra-920/) OR | 1

| 130fs, and average power >1W Example suppliers: TOPTICA, SPARKLASER, COHERENT | | | ALCOR X-Sight (https://spark-lasers.com/wp-content/uploads/2022/10/Specs_sheet_ALCOR_09-2022-B.pdf)

Dustin; purchase; USB-hub (7) ports; Deltaco (https://www.dustin.no/product/5010756784/usb-hub-7-ports-usb-30-black); Thorlabs; BNC to SMA Male Connector; CA2848 (https://www.thorlabs.com/thorproduct.cfm?partnumber=CA2848); SMA-to- SMA cable; CA2912 (https://www.thorlabs.com/thorproduct.cfm?partnumber=CA2948); Power supply for μTLENS driver; TPS002 (https://www.thorlabs.com/thorproduct.cfm?partnumber=TPS002)

95 | Thorlabs | purchase | BNC Male to BNC Male & BNC adapters Female-Female | CA3136 (https://www.thorlabs.com/thorproduct.cfm?partnumber=CA3136) T3283 (https://www.thorlabs.com/thorproduct.cfm?partnumber=T3283) | >10 >10
97 | Thorlabs | purchase | SMC connector SMA female to BNC male | PAA101 (https://www.thorlabs.com/thorproduct.cfm?partnumber=PAA101) CA2606 (https://www.thorlabs.com/thorproduct.cfm?partnumber=CA2606) | 2 1

### Software

100 | Vidrio Technologies LLC | purchase | Open-source software for the whole system | ScanImage 2021 (https://vidriotechnologies.com/scanimage/) | | 1
101 | Others | free or purchase | See Protocol S4 | NA | NA | 1

## MINI2P miniscope 2023 (new items #A102,B104,C118,D107)

### Mechanical components

Kavli NTNU; self-made; Stitching Adapters (PEEK CF30 black); GitHub

102 | Kavli NTNU | self-made | #A102_2023 Scope Body P1 (PEEK CF30 black) | GitHub | | 1
103 | Kavli NTNU | self-made | Scope Body P2 (PEEK CF30 black) MINI2P 2022 | GitHub | | 1
104 | Kavli NTNU | self-made | #B104_2023 Scopebody P3 V2 (PEEK CF30 black) | GitHub | | 1

Kavli NTNU; self-made; Baseplate (Al6061 black anodized); GitHub

107 | Kavli NTNU | self-made | #D107_2023 TLens testing holder (Al6061 black anodized) | GitHub | | 1
108 | FandWay TRfastenings | purchase | Screws for MINI2P: M1.2 x 3.0/4.0 pan head M1.6x 2.5 DIN916 – 45H (black) | M1.2cap (https://www.amazon.co.uk/HanTof-800pcs-Kinds-Screws-Assortment/dp/B07TKMT6BF) M1.6set (https://www.trfastenings.com/Products/Catalogue/Screws-and-Bolts/Set-Screws/Hexagon-Socket-Drive/Cup-Point/TR00015648-000?rank=1) | NA | 2 >10

### Optical components

109 | Domilight | purchase | Scan Lens | D0166 (http://www.domilight.com/) | 1
110 | Fuzhou Sunlight Technology | purchase | Dichroic Mirror | DMSP0405 (http://sunlight-tec.com/en/cpzx.asp) | 1
111 | Domilight | purchase | Objective1 Water+glass | D0213-3X (http://www.domilight.com/) | 1
112 | Domilight | purchase | Objective2 Air | D0254-3X (http://www.domilight.com/) | 1
113 | Domilight | purchase | Objective3**** Air+glass | D0309-3X (http://www.domilight.com/) **** | 1

114 | Polight | purchase | μTLENS & accessories 4 Stacked μTLENS
| | | Male-pin

μTLENS-NIR-D-45 (https://www.polight.com/Products/tlens/default.aspx)

Mill-max1 (https://www.digikey.com/en/products/detail/mill-max-manufacturing-corp/852-10-100-10-001000/279660)

1

1

### Electrical components

Mirrorcle; purchase; FAST MEMS (MEMS-F); A7M10.2-1000AL (https://www.mirrorcletech.com/wp/products/mems-mirrors/dual/integrated/); Large-angle MEMS (MEMS-L); A3I12.2-1200AL (https://www.mirrorcletech.com/wp/products/mems-mirrors/dual/integrated/); Kavli NTNU Digi-key; MEMS PCB & others Female-pin; LABmaker (https://www.labmaker.org/collections/2-photon-miniscope-mini2p) Mill-max2 (https://www.digikey.no/no/products/detail/mill-max-manufacturing-corp/853-93-100-10-001000/279662)

### Others/ New components 2023

118 | Kavli NTNU | Self-made | #C118 (new!) MEMs locker (PEEK-CF30 black anodized) | GitHub | 1
119 | Kavli NTNU | Self-made | Dummy scope | GitHub (https://github.com/kavli-ntnu/MINI2P_toolbox/tree/main/Hardware/Headbar) | 5-10
120 | Kavli NTNU | Self-made | Headbars for (3 types) CA1 V1 MEC + 5mm cannular See prism assemble | GitHub (https://github.com/kavli-ntnu/MINI2P_toolbox/tree/main/Hardware/Headbar) GitHub Prism assemble (https://github.com/kavli-ntnu/MINI2P_toolbox/tree/main/Hardware/Prism%20Assemby) | >10
121 | Sunlight | purchase | Glass plugs 4.6x1.5mm | Sunlight | >2
122 | Sunlight | purchase | Cover slips Dia5x0.15mm | Sunlight | 1
123 | ThermoFisher | purchase | Beads FluoSpheres Carboxylate yellow/green (505-515) (dissolve with ethanol/distilled water) | F8823 (https://www.thermofisher.com/order/catalog/product/F8823) | 1

Thorlabs; purchase; Quick-connect goniometers; XRNG2/M (https://www.thorlabs.com/thorproduct.cfm?partnumber=XRNG2/M)

* NKT updated this product to K50-060-70 since 2021. The outer diameter of the old product

### (K50-060-00) and the new one (K50-060-70) is different!

NKT has a new fiber available since 2023: K60-060-PM (in protocols referred as HC-920-PM). ** TUB-1.8x7-0.155 fits HC-920: K50-060-00. If your HC-920 is K50-060-70, the order name of this component should be TUB-1.8x6.5-0.127. The 3D models for both components are on GitHub

### now. “33-GlassFlange” is TUB-1.8x7-0.155, “33-GlassFlange-for new HC-920” is for TUB-

1.8x6.5-0.127.
*** MRA12-P01 for the new K50-060-PM was replaced by MRA12-E03 (https://www.thorlabs.com/thorproduct.cfm?partnumber=MRA12-E03)

**** A lighter version (less 125mg) of this objective is available with ordering name: D0309.

### Note on the 3D Model & 2D Drawings connected to the Machining & Price List above:

In the attached files are the 3D drawings in STEP format that can be opened in multiple programs where three-dimensional data is represented. These 3D models are available for all the components of the MINI2P platform (both in-house and items bought). However, the 2D drawings given in DWG format are only for home-made components, whereas a link is provided to the 2D drawings of all the other bought components, which are accessible on the supplier's website.

124 | Thorlabs | purchase | Kinematic rotation mount (for distortion grid setup) | KS1RS (https://www.thorlabs.com/thorproduct.cfm?partnumber=KS1RS) | 1
126 | LabMaker | purchase | Sacrificial connector v1 6-position connector with flex PCB | LabMaker (https://www.labmaker.org/collections/2-photon-miniscope-mini2p/products/mini2p-sacrificial-connector-v1) | 1
127 | LabMaker | purchase | Scope cable harness v1 (assembled, replacing items 47-50) | LabMaker (https://www.labmaker.org/collections/2-photon-miniscope-mini2p/products/mini2p-scope-cable-harness-v1) | 1
128 | LabMaker | purchase | Coupling box v1 (Mounted with all optical components) | LabMaker (https://www.labmaker.org/collections/2-photon-miniscope-mini2p/products/mini2p-coupling-box-v1) | 1
129 | Spark Laser | purchase | NEW! ALCOR 920-MINI2P laser «Plug and Play» with coupled fiber | ALCOR 920-Mini2P

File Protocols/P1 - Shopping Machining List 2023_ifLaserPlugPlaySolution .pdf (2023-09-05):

## P1– Shopping & Machining List

Item
ID
Source | Accessibility | Name/Description
(Material for self-made)
Link | Image | Quantity

## General tools

a. | Thorlabs | purchase | Spanner wrench 1 | SPW30 (https://www.thorlabs.com/thorproduct.cfm?partnumber=SPW603) | 1
b. | Thorlabs | purchase | Fiber stripping tool | FTS4 (https://www.thorlabs.com/thorproduct.cfm?partnumber=FTS4) | 1
c. | Thorlabs | purchase | Fiber cleaver | XL411 (https://www.thorlabs.com/thorproduct.cfm?partnumber=XL411) | 1
d. | Thorlabs | purchase | Spanner wrench 2 | SPW602 (https://www.thorlabs.com/thorproduct.cfm?partnumber=SPW602) | 1
e. | Thorlabs | purchase | UV Curing LED system | CD20K2 (https://www.thorlabs.com/thorproduct.cfm?partnumber=CS20K2) | 1
f. | Thorlabs | purchase | Handheld laser source (635nm) Single mode patch cable | HLS635 (https://www.thorlabs.com/thorproduct.cfm?partnumber=HLS635) P1-630Y-FC-2 (https://www.thorlabs.com/thorproduct.cfm?partnumber=P1-630Y-FC-2) | 1 1
g. | Thorlabs | purchase | Power and energy meter Photodiode power sensor | PM100D (https://www.thorlabs.com/thorproduct.cfm?partnumber=PM100D) S121C (https://www.thorlabs.com/thorproduct.cfm?partnumber=S121C) | 1 1

h. | Thorlabs | purchase | Green LED (530nm) T-Cube LED Driver Power supply | M530F2 (https://www.thorlabs.com/thorproduct.cfm?partnumber=M530F2) LEDD1B (https://www.thorlabs.com/thorproduct.cfm?partnumber=LEDD1B) KPS201 (https://www.thorlabs.de/thorproduct.cfm?partnumber=KPS201) | 1 1 1
i. | Thorlabs | purchase | NIR detector card | VRC4 (https://www.thorlabs.com/thorproduct.cfm?partnumber=VRC4) | 1
j. | Thorlabs | purchase | Lens cleaning tissues | MC-5 (https://www.thorlabs.com/thorproduct.cfm?partnumber=MC-5) | 1
k. | RS | purchase | Foam cotton bud & swabs | Swabs (https://no.rs-online.com/web/p/cotton-buds/4077931) | 1
l. | Thorlabs | purchase | Optical adhesive | NOA61 (https://www.thorlabs.com/thorproduct.cfm?partnumber=NOA61) | 1
m. | Thorlabs | purchase | Splice protector sleeve | SPS60 (https://www.thorlabs.com/thorproduct.cfm?partnumber=SPS60) | 1-2
n. | Thorlabs | purchase | Distortion grid with 50um grid spacing Fluorescent marker | R1L3S3P (https://www.thorlabs.de/thorproduct.cfm?partnumber=R1L3S3P) - | 1 1
o. | Winjee | purchase | Silicone rubber back glue | 704 (https://www.amazon.co.uk/WINJEE-Silicone-Industrial-Adhesive-Rubber/dp/B07WBZBYY5) | 1
p. 3M | Loctite | purchase | Epoxy (black) Super glue | DP420 (https://www.3m.co.uk/3M/en_GB/p/d/b40066431/) 415 (https://www.henkel-adhesives.com/us/en/product/instant-adhesives/loctite_415.html) | 1 1

q. | Ahlsell | purchase | Heat gun | link (https://www.ahlsell.no/33/verktoy/elektriske-handverktoy-og-maskiner/elektriske-handverktoy-nettilkoblet/varmluftpistoler/8805144-f63a2a60/) | 1
r. | APE | purchase | Pulsed Check autocorrelator | APE-NX (https://www.ape-berlin.de/en/autocorrelator/pulsecheck/) | 1
s. | Thorlabs | purchase | Base to fixate Pulse Check on Optical Breadboard | MB2025/M (https://www.thorlabs.com/thorProduct.cfm?partNumber=MB2025/M) | 1
t. | Fabory | purchase | M2x5H Philips 7985225 | M2screws (https://www.fabory.com/en/cross-recessed-raised-cheese-head-screw-phillips-din-7985-h-stainless-steel-a2-m2x5/p/51340020005) | >10
u. | TRfastenings | purchase | M3x3mm Pan Head PoziDriv Machine Screw DIN7985 | M3x3 (https://www.trfastenings.com/products/Catalogue/Screws-and-Bolts/Machine-Screws/Pan-Head/PoziDriv) | >3
v. | Thorlabs | purchase | M4 capscrews kit | HW-KIT1/M (https://www.thorlabs.com/thorProduct.cfm?partNumber=HW-KIT1/M) | 1
w. | Elfa Distrelec | purchase | Air duster Green PRF | PRF 4-44 (https://www.elfadistrelec.no/en/compressed-air-spray-405-ml-prf-prf-green-trigger-44-nfl-405ml/p/30098436?q=&pos=2&origPos=2&origPageSize=50&track=true) | 1
x. Surface | Solutions | purchase | Black rubber spray | SS black (https://www.paintshop.no/home/303-blouse.html) | 1
y. | Elfa Distrelec | purchase | Tweezers Carbon Fibre Forceps | 301-51-451 (https://www.elfa.se/en/tweezer-carbon-fibre-flat-squared-straight-130mm-ideal-tek-279cfr-sa/p/30151451) 11270-20 (https://www.finescience.com/en-US/Products/Forceps-Hemostats/Dumont-Forceps/Dumont-7b-Forceps/11270-20) | 1 1

## Core optics module

### Mechanical components

1 | Thorlabs | purchase | Nexus breadboard | B3045L (https://www.thorlabs.com/thorproduct.cfm?partnumber=B3045L) | 1

Thorlabs; purchase; Sorbothane feet; AV6/M (https://www.thorlabs.com/thorproduct.cfm?partnumber=AV6/M); Fiber adapter plate; SM1SMA (https://www.thorlabs.com/thorproduct.cfm?partnumber=SM1SMA#ad-image-0); Adjustable mirror mount; POLARIS-K05S2 (https://www.thorlabs.com/thorproduct.cfm?partnumber=POLARIS-K05S2); Rotation mount & M3 screw; MRM05/M (https://www.thorlabs.com/thorproduct.cfm?partnumber=MRM05/M); M6 cap screws kit; HW-KIT2/M (https://www.thorlabs.com/thorproduct.cfm?partnumber=HW-KIT2/M); 3 axis Microblock stage; MBT616D/ M (https://www.thorlabs.com/thorproduct.cfm?partnumber=MBT616D#ad-image-0); Purchase; Compatible flexure stage mount; HCS020 (https://www.thorlabs.com/thorproduct.cfm?partnumber=HCS020)

7 | Wolida | purchase | Heat shrinkage tubings Wolida Ø0.6/0.4mm 2:1 ratio 2.5mm Distrelec 3mm | Tube1 (https://m.alibaba.com/product/60562691813/WOLIDA-heat-shrinkable-tube-black-flame.html) Tube2 (https://www.amazon.com/100FT-BLACK-HEAT-SHRINK-TUBING/dp/B006HU7XCA) Tube3 (https://www.distrelec.biz/en/heat-shrink-tubing-3mm-black-polyolefin-10m-hellermanntyton-his-bk/p/15505468) | 3
9 | Thorlabs | Purchase | XYZ Translation stage & right-angle bracket | MT3A/M (https://www.thorlabs.de/thorproduct.cfm?partnumber=MT3A/M) AB90E/M (https://www.thorlabs.com/thorproduct.cfm?partnumber=AB90E/M#ad-image-0) | 1
11 | Thorlabs | Purchase | Fiber clamp holds fiber Bare fiber adapter &Flat base to glue into (e.g.) | HFF001 (https://www.thorlabs.com/thorproduct.cfm?partnumber=HFF001) S140-BFA (https://www.thorlabs.com/thorproduct.cfm?partnumber=S140-BFA) XT95P3 (https://www.thorlabs.de/thorProduct.cfm?partNumber=XT95P3) | 1 3 1

Thorlabs; purchase; Fixed mounting bracket; AMA007/M (https://www.thorlabs.com/thorproduct.cfm?partnumber=AMA007/M); Kinematic cage cube; DFM1T3 (https://www.thorlabs.de/thorproduct.cfm?partnumber=DFM1T3); Kinematic cage cube base; DFM1B (https://www.thorlabs.com/thorproduct.cfm?partnumber=DFM1B/M); Lens tubes; SM1L05 (https://www.thorlabs.com/thorproduct.cfm?partnumber=SM1L05); End cap for machining; SM1CP2M (https://www.thorlabs.com/thorproduct.cfm?partnumber=SM1CP2M); Coupler; SM1T2 (https://www.thorlabs.com/thorproduct.cfm?partnumber=SM1T2); Post mounting adapter; SHM1/M (https://www.thorlabs.com/thorproduct.cfm?partnumber=SHM1/M)

13 | Thorlabs | purchase | SM05 Threaded adapter to red laser source FC/PC Fiber Collimation (linked to items f) | AD1109F (https://www.thorlabs.com/thorproduct.cfm?partnumber=AD1109F) F230FC-B (https://www.thorlabs.com/thorProduct.cfm?partNumber=F230FC-B) | 1 1
19 | Thorlabs | purchase | Optical beam shutter with controller for PMT | SHB1 (https://www.thorlabs.com/thorproduct.cfm?partnumber=SHB1#ad-image-0) | 1
21 | Kavli NTNU | self-made | Coupling box (Al7075 with sand spray) | Github(1) | 1
22 | Kavli NTNU | self-made | Coupling box cap (Al7075 with sand spray) | Github(1) | 1

Kavli NTNU; self-made; Coupling holder (Stainless steel); Github(1); Coupling protector (Al anodized); Collimator assemble tool (Al6061); Collimator holder (Al6061 black anodized)

27 | Kavli NTNU | self-made | Control box shell (Al6061 black anodized) | Github(1) | 1
28 | Kavli NTNU | self-made | Control box cap (Al6061 black anodized) | Github(1) | 1

### Optical components

29 | Femtosecond laser with center wavelength at 920nm, 80MHz, pulse width 100-130fs, and average power >1W Example suppliers: TOPTICA, SPARKLASER, COHERENT | purchase | Laser source Spark Laser offers higher positive GDD (up to 120 000 fs² ) | Example types: FemtoFibe r ultra 920 (https://www.toptica.com/products/psfs-fiber-lasers/femtofiber-ultra/femtofiber-ultra-920/) ALCOR 920 X-Sight (https://spark-lasers.com/wp-content/uploads/2022/10/Specs_sheet_ALCOR_09-2022-B.pdf) | 1 OR 1
30 | LabMaker | modify | Tapered fiber bundle (TFB) XMLG, Ø.027”x98.4”[2.5 m] Drawing C54706.04 PRODUCTION DISCONTINUED! Grin Fiber Bundle (GFB) New solution! with items: 30.1 Fiber Bundle by SCHOTT Part Number 1840314 Drawing C54706.1X | 1838003 (https://www.schott.com/products/flexible-light-guides) 1840314 | 1

| 30.2 AR windows by Sunlight (dia1.8x0.2mm,S1:HT T>99%@450-700nm, AOI=0deg) 30.3 GRIN lens #64-520 Or #64-526 (1.8mm Dia, 670nm DWL, 0.23mm WD) 30.4 GFB holder Note: GFB is compatible with version2 of Scopebody P3 (see item #104_2023) | WIN1.8x0. 2-S1AR450-700 #64-520 (https://www.edmundoptics.com/p/18mm-dia-670nm-dwl-023mm-wd-uncoated-grin-lens/19232/) Or #64-526 (https://www.edmundoptics.eu/p/18mm-dia-810nm-dwl-023mm-wd-uncoated-grin-lens/19238/) GitHub (https://github.com/kavli-ntnu/MINI2P_toolbox/tree/main/Hardware/GFB)

NKT Photonics; purchase; (≈2.2-2.4m) Hollow-core PCF, HC-920 *; K60-060-PM (https://www.nktphotonics.com/lasers-fibers/product/hollow-core-photonic-crystal-fibers/) *; Fuzhou Sunlight Technology; Glass rods (ZF62); GLA-10x150-AR800-1100 (http://sunlight-tec.com/en/cpzx.asp)

33 | Fuzhou Sunlight Technology | purchase | Inside ∅ 0.126 − 0.128mmmm) Glass flange ** (6.5mm length | TUB-1.8x6.5-0.127 (http://sunlight-tec.com/en/cpzx.asp) ** | 2

Thorlabs; purchase; Shortpass filter; FESH0750 (https://www.thorlabs.com/thorproduct.cfm?partnumber=FESH0750); Dichroic mirror; DMLP567 R (https://www.thorlabs.com/thorproduct.cfm?partnumber=DMLP567R); Aspheric condenser lens; ACL25416 U-A (https://www.thorlabs.com/thorproduct.cfm?partnumber=ACL25416U-A)

34 | Thorlabs | purchase | Prisms*** direct light from the seed laser up to the HC-920 fiber | MRA12-E03 (https://www.thorlabs.com/thorProduct.cfm?partNumber=MRA10-E03) *** | 8
35 | Thorlabs | purchase | Emission filter 525 nm green channel | MF525-39 (https://www.thorlabs.com/thorproduct.cfm?partnumber=MF525-39) | 1
36 | Thorlabs | purchase | Emission filter 630 nm red channel | MF630-69 (https://www.thorlabs.com/thorproduct.cfm?partnumber=MF630-69) | 1

Thorlabs; purchase; Coupling lens; C230TMD-B (https://www.thorlabs.com/thorproduct.cfm?partnumber=C230TMD-B); Half-Wave plate; WPHSM05 -915 (https://www.thorlabs.com/thorproduct.cfm?partnumber=WPHSM05-915); Protected silver mirrors; PF05-03-P01 (https://www.thorlabs.com/thorproduct.cfm?partnumber=PF05-03-P01); Edmund Optics; Collimating lens; #84-128 (https://www.edmundoptics.com/p/2mm-dia-x-4mm-fl-vis-nir-coated-achromatic-lens/27236/)

### Electrical components

Digikey; purchase; BNC to SMA cables; CCBNS-MM-RG174-36 (https://www.digikey.no/product-detail/no/crystek-corporation/CCBNS-MM-RG174-36/744-1249-ND/1767703); DSUB15 connector plug (male); 472-859 (https://no.rs-online.com/web/p/d-sub-connectors/0472859/); Backshell; 765-9448 (https://no.rs-online.com/web/p/d-sub-connectors/7659448)

44 | Mirrorcle Technologies | purchase | MEMS driver (controller) BDQ PicoAmp 5.4 T180 | DR-11-055-00 (https://www.mirrorcletech.com/wp/products/hardware/drivers/analog/) | 1

purchase; DSUB15 Connector Socket (female); 472-865 (https://no.rs-online.com/web/p/d-sub-connectors/0472865/); Digikey; 6-pin connector for MEMS; FH19C-6S-0.5SH(10) (https://www.digikey.no/product-detail/no/hirose-electric-co-ltd/FH19C-6S-0-5SH-10/H125824CT-ND/9360234); Thorlabs; μTLens Driver; KPZ101 (https://www.thorlabs.com/thorproduct.cfm?partnumber=KPZ101)

50 | Industrifil | purchase | (6 colours of ≈2.5m) Single wire cables | UAA-3607 (http://www.industrifil.com/insulated.html) | 6

52 | Thorlabs | purchase | PMT | PMT2101/ M (https://www.thorlabs.com/thorproduct.cfm?partnumber=PMT2101/M) | 2
53 | Thorlabs | purchase | Controller for shutter | SHB1 (https://www.thorlabs.de/thorproduct.cfm?partnumber=SHB1#ad-image-0) | 1

## Scope mounting module

### Mechanical components

Thorlabs; purchase; Aluminum optical breadboard; B3060A (https://www.thorlabs.com/thorproduct.cfm?partnumber=B3060A); Sorbothane feet; AV6/M (https://www.thorlabs.de/thorproduct.cfm?partnumber=AV6/M); Precision construction rail L=400mm; XT95B-400 (https://www.thorlabs.com/thorproduct.cfm?partnumber=XT95B-400); Post Mounting Clamp; C1545/M (https://www.thorlabs.com/thorproduct.cfm?partnumber=C1545/M); Manual Rotation Stage; RP03/M (https://www.thorlabs.com/thorproduct.cfm?partnumber=RP03/M); Base for item 58; XT95P3 (https://www.thorlabs.com/thorproduct.cfm?partnumber=XT95P3); Optical post; TR75/M (https://www.thorlabs.com/thorproduct.cfm?partnumber=TR75/M)

56 | Thorlabs | purchase | One-sided construction rail Black Anodized (95x500 mm) | XT95SD-500 (https://www.thorlabs.com/thorproduct.cfm?partnumber=XT95SD-500) | 2
57 | Thorlabs | purchase | Rail carriage suitable for sliding onto item 58 | XT95RC4/ M (https://www.thorlabs.com/thorproduct.cfm?partnumber=XT95RC4/M) | 2

63 | Thorlabs | modify | Running wheel hardboard | Github, TB4 (https://www.thorlabs.com/thorproduct.cfm?partnumber=TB4) | 1/4
64 | Thorlabs | purchase | M6 spacers & washers | W25S050 (https://www.thorlabs.de/thorproduct.cfm?partnumber=W25S050) | >4
65 | Thorlabs | purchase | Spacer on both sides of wheel | PS1M (https://www.thorlabs.com/thorproduct.cfm?partnumber=PS1M) | 2
66 | SKF | purchase | Bearing OD 19mm ID 6mm | 626-2Z (https://no.rs-online.com/web/p/ball-bearings/2867849/) | 1
67 | Thorlabs | purchase | Right-angle clamp | RSA90/M (https://www.thorlabs.de/thorproduct.cfm?partnumber=RSA90/M) | 1
68 | Thorlabs | purchase | Pillar posts | RS50/M (https://www.thorlabs.com/thorproduct.cfm?partnumber=RS50/M) | 2

Thorlabs; purchase; Universal post holder; UPH100/M (https://www.thorlabs.com/thorproduct.cfm?partnumber=UPH100/M#ad-image-0); Adapter camera-lens; SM1A10Z (https://www.thorlabs.com/thorproduct.cfm?partnumber=SM1A10Z); Kavli NTNU; self-made; MINI2P Holder P1 (Al6061); Github(1); MINI2P Holder P2 (Al6061); MINI2P Holder P3 (Stainless steel)

70 | Thorlabs | purchase | Locking Ball and Socket Mount; to support LEDs near Tracking Camera | TRB1/M (https://www.thorlabs.com/thorproduct.cfm?partnumber=TRB1/M) | 8
75 | Kavli NTNU TRfastenings | self-made | MINI2P Holder P4 & screw (Stainless steel) M2.5x5 cap head hexagon socket drive screw, DIN912 | Github(1) M2.5cap (https://www.trfastenings.com/Products/Catalogue/Screws-and-Bolts/Machine-Screws) | 1 1


| | | MINI2P holder P4 version 2 (NEW!) Holder for scope assembly | Github | 1
76 | Kavli NTNU | self-made | Wheel Holder (Stainless steel) | Github | 1
77 | Kavli NTNU TRfastenings | self-made | Headbar holder & screw (Titanium alloy) M3x3mm Pan Head PoziDriv Machine Screw, zinc & clear, DIN7985 | Github M3x3 (https://www.trfastenings.com/Products/Catalogue/Screws-and-Bolts/Machine-Screws/Pan-Head/PoziDriv) | 1 2

### Optical and electrical components

78 | Thorlabs RS | purchase | LED & Accessories 850nm IR LED Array Light Source LED 5m cable Adapter Supply Power for LED | LIU850A (https://www.thorlabs.com/thorproduct.cfm?partnumber=LIU850A) 780-0087 (https://no.rs-online.com/web/p/industrial-automation-cable-assemblies/7800087) 301-29-731 (https://www.elfadistrelec.no/no/koblingsmuffe-1x5-5mm-rett-rnd-connect-rnd-205-00911/p/30129731) 136-1345 (https://no.rs-online.com/web/p/ac-dc-adapters/1361345) | 1 1 1 1


79 | Thorlabs | purchase | Zelux 1.6 MP Monochrome CMOS Camera & adapter SM1 to C-Mount | CS165MU/ M (https://www.thorlabs.com/thorproduct.cfm?partnumber=CS165MU/M) SM1A10Z (https://www.thorlabs.de/thorproduct.cfm?partnumber=SM1A10Z) | 1 1
80 | Edmund Optics | purchase | Lens focal length 4.5mm Or 8.5mm for lateral and frontal camera to control head fixation | 4.5mm (https://www.edmundoptics.com/p/45mm-c-series-fixed-focal-length-lens/29328/) 8.5mm (https://www.edmundoptics.com/p/85mm-f8-23-hpi-series-fixed-focal-length-lens/40682/) | 1
81 | Edmund Optics | purchase | Basler camera for Animal Tracking 16mm EFL Camera Lens Shortpass Filter 875nm | acA2040-90um (https://www.baslerweb.com/en/products/cameras/area-scan-cameras/ace/aca2040-90um/) MVL16M2 3 (https://www.thorlabs.com/thorproduct.cfm?partnumber=MVL16M23) #86-106 (https://www.edmundoptics.com/p/875nm-25mm-diameter-od-4-shortpass-filter/28593/) | 1 1 1

82 Physik
Instrumente
(PI)
purchase | DC Motors | M- 112.2DG (https://www.physikinstrumente.com/en/products/linear-stages/stages-with-stepper-dc-brushless-dc-bldc-motors/m-110-m-111-m-112-compact-linear-stage-412418433/)

3

## Mobile cart and controlling system

### Mechanical and electrical components

83 | Thorlabs | purchase | Mobile cart | POC001 (https://www.thorlabs.com/thorproduct.cfm?partnumber=POC001) | 1
84 | Thorlabs | purchase | Optical breadboard 600x900x55mm | PBG52506 (https://www.thorlabs.com/thorproduct.cfm?partnumber=PBG52506) | 1
85 | Thorlabs | purchase | Optional drawer | POD001 (https://www.thorlabs.com/thorProduct.cfm?partNumber=POD001) | 1
86 | Schroff | purchase | 19-inch rack | Ref 721-2708 (https://no.rs-online.com/web/p/rackmount-cases/7212708/) | 1
87 | McMASTER-CARR | purchase | Span-in nuts | 90680A729 (https://www.mcmaster.com/90680A729/) | 10
88 | Dell | purchase | Workstation is an Intel core i9 with operating windows 10 Pro | 7080 (https://www.dell.com/en-us/work/shop/desktops-all-in-one-pcs/optiplex-7080-tower-and-small-form-factor/spd/optiplex-7080-desktop) | 1
89 | Dell | purchase | (32”to 49”) curved LED-backlit LCD5K2K monitor | Monitor (https://www.dell.com/en-uk/shop/dell-ultrasharp-40-curved-wuhd-monitor-u4021qw/apd/210-ayjf/monitors-monitor-accessories) | 1
90 | Vidrio Technologies LLC | purchase | vDAQ card provides data acquisition and control of Laser, µTLens, shutter, among others | V-vDAQ.R1 (https://vidriotechnologies.com/vdaq/) | 1
91 | Vidrio Technologies LLC | purchase | vDAQ breadboard | V-vDAQ.R1 (https://vidriotechnologies.com/vdaq/) | 1
92 | Physik Instrumente (PI) | purchase | Motion controller for PI motors | C-884.4DC (https://www.physikinstrumente.com/en/products/controllers-and-drivers/motion-controllers-drivers-for-linear-torque-stepper-dc-servo-motors/c-8844dc-c-8846dc-m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) | 1
93 | Femtosecond laser with center wavelength at 920nm, 80MHz, pulse width 100- | purchase | Controller for 920nm laser | Example types: FFUltra92 0 (https://www.toptica.com/products/psfs-fiber-lasers/femtofiber-ultra/femtofiber-ultra-920/) OR | 1

| 130fs, and average power >1W Example suppliers: TOPTICA, SPARKLASER, COHERENT | | | ALCOR X-Sight (https://spark-lasers.com/wp-content/uploads/2022/10/Specs_sheet_ALCOR_09-2022-B.pdf)

Dustin; purchase; USB-hub (7) ports; Deltaco (https://www.dustin.no/product/5010756784/usb-hub-7-ports-usb-30-black); Thorlabs; BNC to SMA Male Connector; CA2848 (https://www.thorlabs.com/thorproduct.cfm?partnumber=CA2848); SMA-to- SMA cable; CA2912 (https://www.thorlabs.com/thorproduct.cfm?partnumber=CA2948); Power supply for μTLENS driver; TPS002 (https://www.thorlabs.com/thorproduct.cfm?partnumber=TPS002)

95 | Thorlabs | purchase | BNC Male to BNC Male & BNC adapters Female-Female | CA3136 (https://www.thorlabs.com/thorproduct.cfm?partnumber=CA3136) T3283 (https://www.thorlabs.com/thorproduct.cfm?partnumber=T3283) | >10 >10
97 | Thorlabs | purchase | SMC connector SMA female to BNC male | PAA101 (https://www.thorlabs.com/thorproduct.cfm?partnumber=PAA101) CA2606 (https://www.thorlabs.com/thorproduct.cfm?partnumber=CA2606) | 2 1

### Software

100 | Vidrio Technologies LLC | purchase | Open-source software for the whole system | ScanImage 2021 (https://vidriotechnologies.com/scanimage/) | | 1
101 | Others | free or purchase | See Protocol S4 | NA | NA | 1

## MINI2P miniscope 2023 (new items #A102,B104,C118,D107)

### Mechanical components

Kavli NTNU; self-made; Stitching Adapters (PEEK CF30 black); GitHub

102 | Kavli NTNU | self-made | #A102_2023 Scope Body P1 (PEEK CF30 black) | GitHub | | 1
103 | Kavli NTNU | self-made | Scope Body P2 (PEEK CF30 black) MINI2P 2022 | GitHub | | 1
104 | Kavli NTNU | self-made | #B104_2023 Scopebody P3 V2 (PEEK CF30 black) | GitHub | | 1

Kavli NTNU; self-made; Baseplate (Al6061 black anodized); GitHub

107 | Kavli NTNU | self-made | #D107_2023 TLens testing holder (Al6061 black anodized) | GitHub | | 1
108 | FandWay TRfastenings | purchase | Screws for MINI2P: M1.2 x 3.0/4.0 pan head M1.6x 2.5 DIN916 – 45H (black) | M1.2cap (https://www.amazon.co.uk/HanTof-800pcs-Kinds-Screws-Assortment/dp/B07TKMT6BF) M1.6set (https://www.trfastenings.com/Products/Catalogue/Screws-and-Bolts/Set-Screws/Hexagon-Socket-Drive/Cup-Point/TR00015648-000?rank=1) | NA | 2 >10

### Optical components

109 | Domilight | purchase | Scan Lens | D0166 (http://www.domilight.com/) | 1
110 | Fuzhou Sunlight Technology | purchase | Dichroic Mirror | DMSP0405 (http://sunlight-tec.com/en/cpzx.asp) | 1
111 | Domilight | purchase | Objective1 Water+glass | D0213-3X (http://www.domilight.com/) | 1
112 | Domilight | purchase | Objective2 Air | D0254-3X (http://www.domilight.com/) | 1
113 | Domilight | purchase | Objective3**** Air+glass | D0309-3X (http://www.domilight.com/) **** | 1

114 | Polight | purchase | μTLENS & accessories 4 Stacked μTLENS
| | | Male-pin

μTLENS-NIR-D-45 (https://www.polight.com/Products/tlens/default.aspx)

Mill-max1 (https://www.digikey.com/en/products/detail/mill-max-manufacturing-corp/852-10-100-10-001000/279660)

1

1

### Electrical components

Mirrorcle; purchase; FAST MEMS (MEMS-F); A7M10.2-1000AL (https://www.mirrorcletech.com/wp/products/mems-mirrors/dual/integrated/); Large-angle MEMS (MEMS-L); A3I12.2-1200AL (https://www.mirrorcletech.com/wp/products/mems-mirrors/dual/integrated/); Kavli NTNU Digi-key; MEMS PCB & others Female-pin; LABmaker (https://www.labmaker.org/collections/2-photon-miniscope-mini2p) Mill-max2 (https://www.digikey.no/no/products/detail/mill-max-manufacturing-corp/853-93-100-10-001000/279662)
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

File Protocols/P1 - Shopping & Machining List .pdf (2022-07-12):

## P1– Shopping & Machining List

Item
ID
Source | Accessibility | Description | Link | Image | Quantity

## General tools

a. | Thorlabs | purchase | Spanner wench 1 | SPW30 (https://www.thorlabs.com/thorproduct.cfm?partnumber=SPW603) | 1
b. | Thorlabs | purchase | Fiber stripping tool | FTS4 (https://www.thorlabs.com/thorproduct.cfm?partnumber=FTS4) | 1
c. | Thorlabs | purchase | Fiber cleaver | XL411 (https://www.thorlabs.com/thorproduct.cfm?partnumber=XL411) | 1
d. | Thorlabs | purchase | Spanner wrench 2 | SPW602 (https://www.thorlabs.com/thorproduct.cfm?partnumber=SPW602) | 1
e. | Thorlabs | purchase | UV Curing LED system | CD20K2 (https://www.thorlabs.com/thorproduct.cfm?partnumber=CS20K2) | 1
f. | Thorlabs | purchase | Handheld laser source (635nm) Single mode patch cable | HLS635 (https://www.thorlabs.com/thorproduct.cfm?partnumber=HLS635) P1-630Y-FC-2 (https://www.thorlabs.com/thorproduct.cfm?partnumber=P1-630Y-FC-2) | 1 1
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

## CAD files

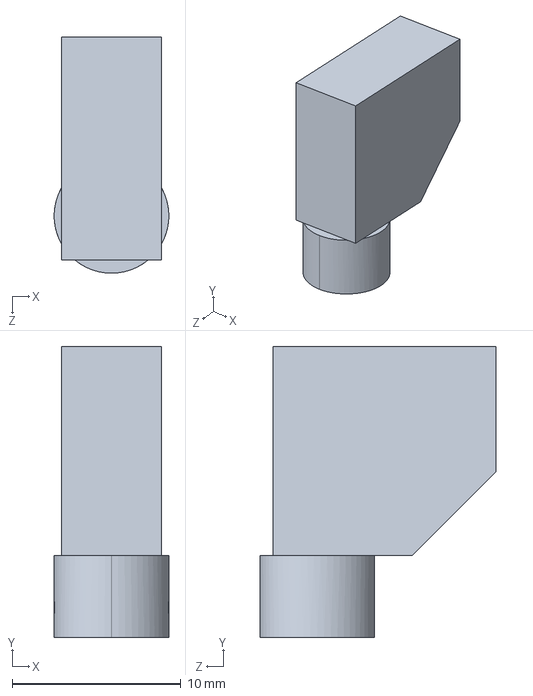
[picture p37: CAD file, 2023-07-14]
Hardware/Dummy/Dummy.STEP
6.80 x 17.2 x 14.0 mm

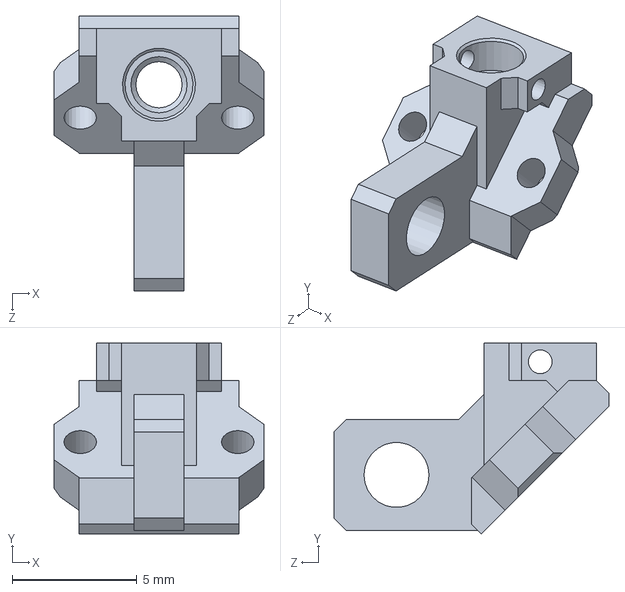
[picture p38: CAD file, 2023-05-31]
Hardware/GFB/ScopeBody P3_V2 .SLDPRT
8.40 x 7.64 x 11.0 mm

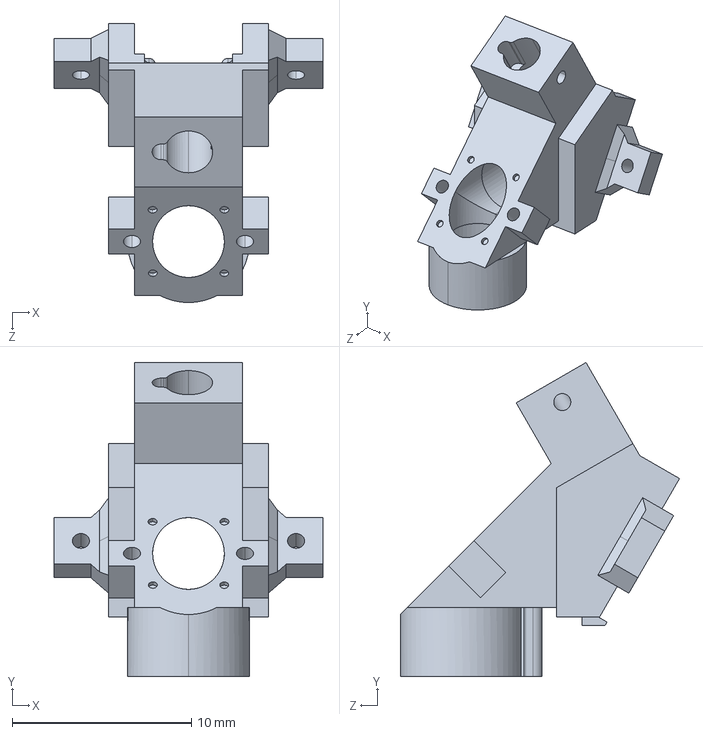
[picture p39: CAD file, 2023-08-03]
Hardware/MINI2P 2023 miniscope/A102_ScopeBody_P1_V2 -2.STEP
15.0 x 17.5 x 15.6 mm

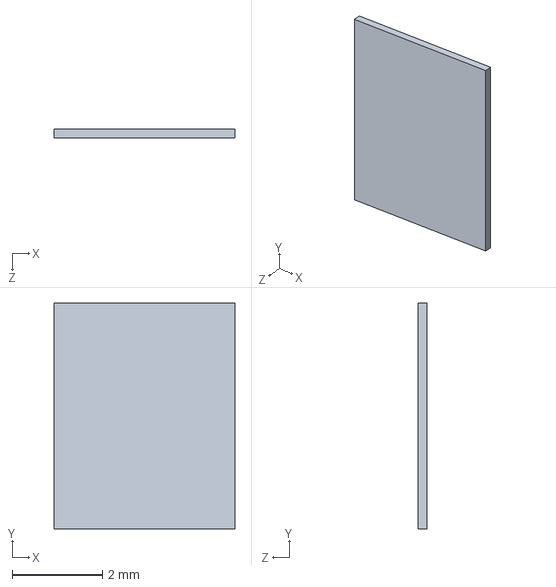
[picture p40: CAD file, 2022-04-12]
Hardware/MINI2P miniscope/110-DM.STEP
4.00 x 5.00 x 0.2 mm

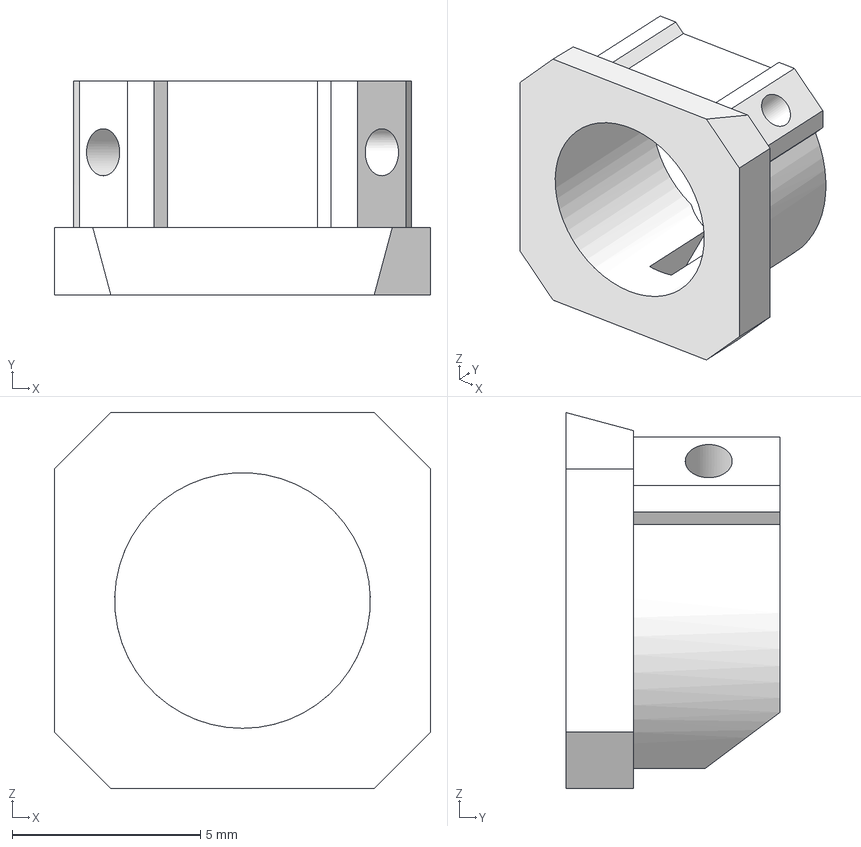
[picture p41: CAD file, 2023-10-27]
Hardware/Stitching Adapter and Baseplate/200um shift shorter stitching adapters/Scopebody adapter_V2_lateralshifting_ML-0000_AP0000.STEP
10.0 x 5.70 x 10.0 mm

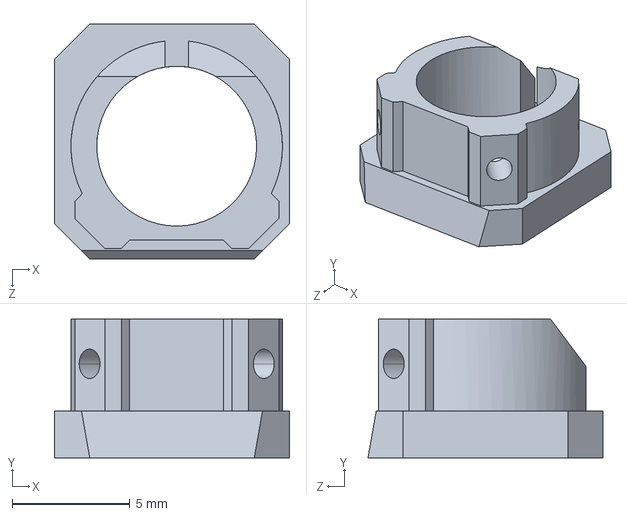
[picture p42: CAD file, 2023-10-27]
Hardware/Stitching Adapter and Baseplate/200um shift stitching adapters/Scopebody adapter_V2_lateralshifting_ML+200_AP+200.STEP
10.0 x 5.90 x 10.0 mm

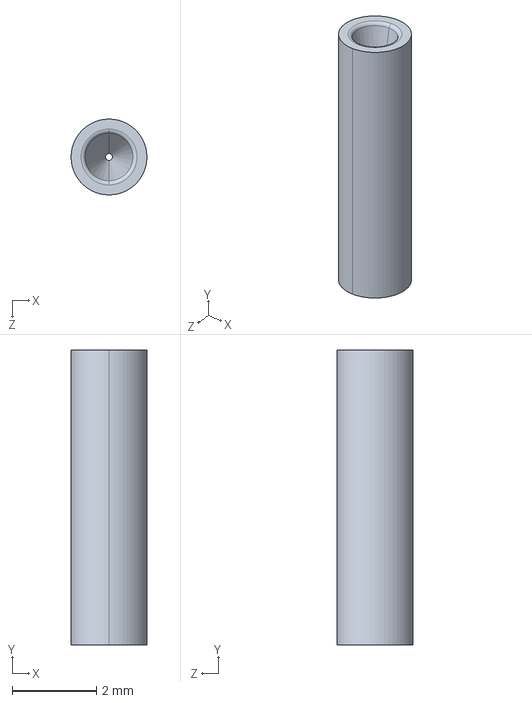
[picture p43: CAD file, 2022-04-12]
Hardware/Core Optics Module/33-GlassFlange .STEP
1.80 x 7.00 x 1.80 mm

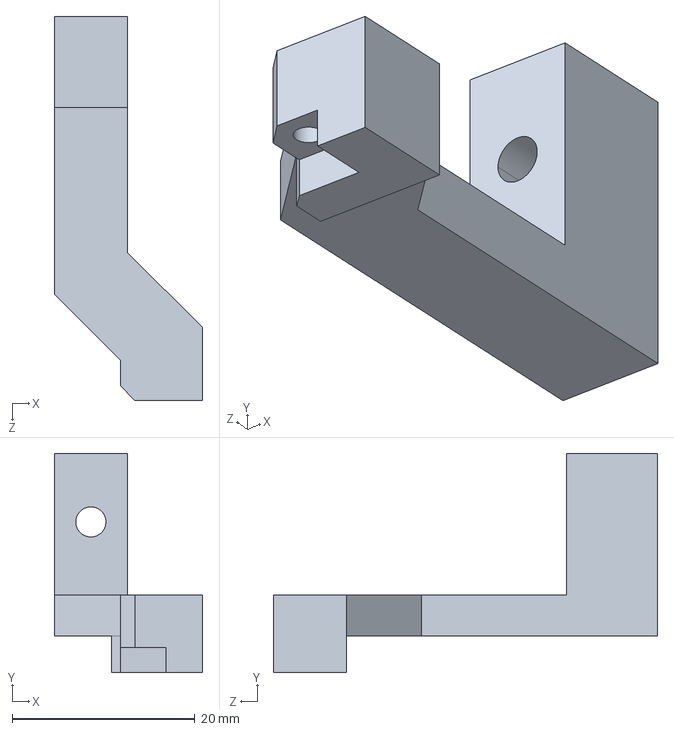
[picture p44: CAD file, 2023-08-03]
Hardware/MINI2P 2023 miniscope/75-MINI2Pholder P4 version 2 .STEP
16.2 x 24.0 x 42.1 mm

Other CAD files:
Hardware/Prism Assemby/Prism assemble.DWG
Hardware/Core Optics Module/25-CollimatorAssembleTool .DWG
Hardware/Core Optics Module/21-CouplingBox_20221120.DWG
Hardware/HC-920 Assemby/26-CollimatorHolder.DWG
Hardware/Headbar/HeadBar_MEC_5mm.DWG
Hardware/Prism Assemby/5mm cannular -2.DWG
Hardware/Scope Mounting Module/75-MINI2Pholder P4 .DWG
Hardware/Stitching Adapter and Baseplate/106-Baseplate.DWG
Hardware/Stitching Adapter and Baseplate/400um shift stitching adapters/Scopebody adapter_V2_lateralshifting_ML+0800_AP0000.DWG
Hardware/Headbar/HeadBar_CA1_5mm.DWG
Hardware/Core Optics Module/22-Cap .DWG
Hardware/Core Optics Module/23-CouplingHolder .DWG
Hardware/Core Optics Module/24-CouplingProtector .DWG
Hardware/Core Optics Module/27-ControlBoxShell .DWG
Hardware/Core Optics Module/28-ControlBoxCap .DWG
Hardware/Core Optics Module/33-GlassFlange - for new HC-920.DWG
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

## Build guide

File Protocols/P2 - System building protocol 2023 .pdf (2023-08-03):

## P2– System building protocol

### Part 1- Core Optics Assembly

Reagents:
- Super glue (Loctite, 415)
- Epoxy adhesive (item p)
- 100% alcohol
- Air duster Green (item w)
- UV curing optical Adhesive (item l)
- Rubber spray (black, item x)

Equipment:
- 2 Tweezers (preferably one flat & one curved)
- Splice Protector Sleeve (item m)
- Lens cleaning tissue (item j)
- Cotton buds & swabs for electronics (item k)
- Heat shrinkage tubings (black, item 7)
- Heat gun (item q)
- Hollow-core 920 nm fiber (HC-920) ≈ 2.5m (item 31)
- Screwdrivers
- Stereomicroscope (Zeiss Trino, WL37166)
- UV curing LED system (item e)
- Components of the coupling module (Table1)
- Components of the fiber coupling setup (Table 2)
- Components of the fiber collimating setup (Table 3)
- Components of the laser alignment (Table 4)
- Components of the detection module (Table 5)
- Components of the controlling module (Table 6)

Table 1: Components of the coupling module
Component Name | Amount | Item Number (see S1, shopping list)
Breadboard | 1 | 1
Sorbothane Feet | 1 | 2
Seed laser | 1 | 29
Coupling box | 1 | 21
Coupling box cap | 1 | 22
Glass rods | 3 | 32
Prisms | 8 | 34
Rotation mount | 1 | 5
Half-wave plate (HWP) | 1 | 41
Adjustable mirror mounts | 2 | 4
Protected silver mirrors | 2 | 42
Cap screws | 4 | 6

Coupling protection | 1 | 24

Table 2: Components of the fiber coupling setup
Coupling holder | 1 | 23
Coupling lenses | 1 | 40
Glass Flange | 1 | 33
Spanner Wrench 1 | 1 | a
XYZ translation stage & right-angle bracket | 1 | 9
Fiber clamp | 1 | 11
Pulse check Autocorrelator | 1 | r
Base to fixate Autocorrelator to Breadboard | 1 | s

Table 3: Components of the fiber collimating setup
3 axis microblock stage | 1 | 8
Fiber Clamp | 1 | 11
Glass Flange | 1 | 33
Fiber stripping tool | 1 | b
Collimator Holder | 1 | 26
Collimating Lenses | 1 | 43
Collimator assemble tool | 1 | 25
Fiber Cleaver | 1 | c

Table 4: Components of the laser alignment
Handheld laser source (635nm) | 1 | f
SM05 threaded adapter to laser source | 1 | 13
Power and energy meter | 1 | g

Table 5: Components of the detection module
Kinematic cage cube | 1 | 14
Kinematic cage cube base | 1 | 15
Emission filter 525 nm green channel | 1 | 35
Emission filter 630 nm red channel | 1 | 36
Shortpass filter | 1 | 37
Dichroic Mirror | 1 | 38
Lens Tubes | 4 | 16
End cap for machining | 1 | 17
Spanner Wrench 2 | 1 | d
Coupler | 3 | 18
Optical beam shutter with controller for PMT | 1 | 19
Post mounting adapter | 1 | 20
Green LED | 1 | h
Aspheric Condenser Lens | 3 | 39
μTlens driver | 1 | 51
PMTs | 2 | 52
Controller for shutter | 1 | 53

Table 6: Components of the controlling module
Control box shell | 1 | 27
Control box cap | 1 | 28
MEMS driver (controller) BDQ PicoAmp 5.4 T180 | 1 | 44
Connectors J1,J2 | 2 | 44
BNC male to BNC male | 8 | 95
DSUB15 to 8xBNC cables
DSUB15 connector plug (male) | 2 | 46
back shell | 2 | 47
DSUB15 connector socket (female) | 2 | 48
DSUB15 to 6-pin (pcb/mems) cable
6-pin connector for MEMS | 1 | 49
Single wire cables | 6 | 50

Cleaning and preparing all components.

Step1. All the custom machined components are cleaned with 100% alcohol. Some components are also cleaned in an ultrasonic bath for 10min including the coupling holder (item 23), collimator holder (item 26), and the glass flanges (item 33).
Step2. Spray all the cleaned components in Step 1 with Air duster (item w) and put them aside in a super clean bench.

Assembling the coupling module.

Step3. Put one half-wave plate (HWP, item 41) into the rotation mount (item 4) and screw the mount from the bottom of the coupling box using a M3 cap screw.
Step4. Fix the seed laser source (item 29) and the coupling box (item 21) on the breadboard (item 1) with four sorbothane feet mounted underneath (item 2). Make sure the entrance of the coupling box is centered to the output of the laser source
Note! To test the laser before using it, align its beam path to the Pulse Check autocorrelator (item r) to optimize the settings to remove the profile side lobes and minimize the pulse fit (≈ 100fs) and measure the maximum average power (≈ 1.2W@ 5V).

Step5. Place right-angle prisms (6 prisms, items 34) on the intended positions inside the coupling box (Fig. S7-B in Zong, et al.,2022, and Fig.1 in this document). Attach the surfaces of the prisms to the inner wall of the coupling box as close as possible. Then add drops of super glue in the contact points. Hold the prisms for a few seconds until they are fixed.
Note! Switch on the laser, place NIR Detection Card after the glued prisms to confirm the prisms were glued correctly, leading to an aligned laser beam path as designed.

Step6. Glue three glass rods (items 32) on the designed positions inside the coupling box (Fig. S7-B in Zong, et al.,2022, and Fig. 1 in this document) Check the laser spot after the glass rods. If centered, drop super glue on contact points of the box’s base and the glass rod and press the latter.
Step7. Make two prism assemblies by gluing a prism (item 34) on top of a thick circular silver mirror (item 42). The thick circular silver mirror acts as an adapter to hold the prism on the mirror mount (see Fig. 2).

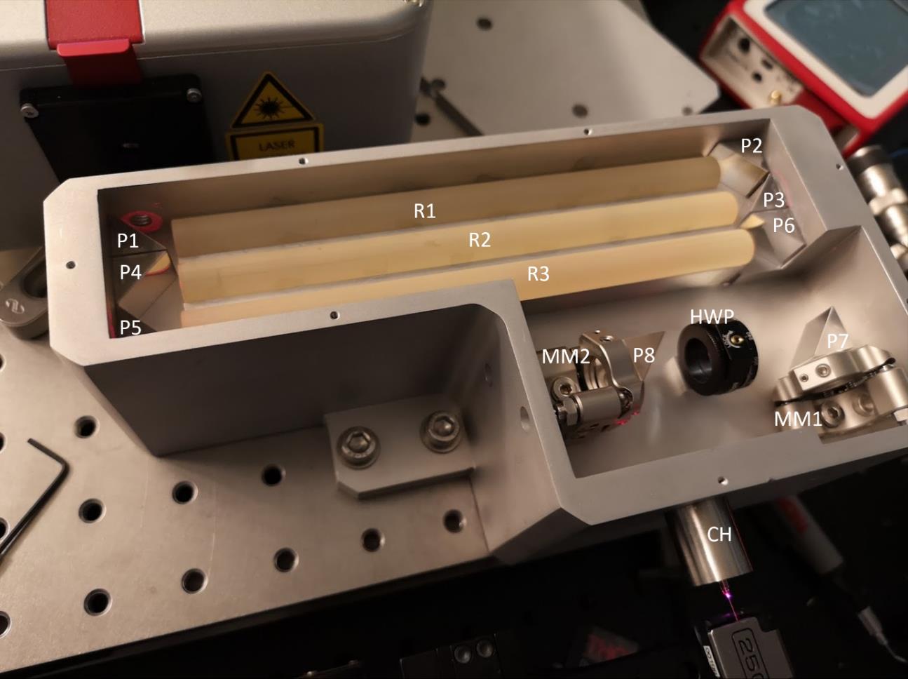
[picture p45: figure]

Figure 1: Placement of coupling box in front of the seed laser, illustrating the components assembled inside as described in this protocol. The right-angle prims are labeled from P1 to P8, glass rods from R1 to R3 glass, Half-wave plate as HWP, mirror mounts as MM1 and MM2 and, finally, coupling holder as CH.

Figure 2: Mirror mount fixated within the coupling box (top) with a schematic of the gluing of the prism on top of a silver mirror (bottom left) with prism centered on the mirror (bottom right).

Step8. Fix the two mirror mounts (item 4) to the coupling box’s base by tightening two M4-screws. The two Hex Adjusters of each mirror mount should face to the two diagonal holes on the vertical walls of the coupling box, such that adjustment of the mirrors’ tilt/pitch can be done from outside of the box.

Step9. Mount the two prism assemblies made in Step 7 on the mirror mounts. Switch on the laser, place a NIR Detector Card before and after P7 and P8 (see Fig.1) to check the alignment of the light path. The laser should pass through the exit hole of the coupling box. If not, adjust mirror mounts until you see the laser from the output hole.
Step10. | Mount the coupling lens (item 40) to the coupling holder (item 23) (see Fig. S7-
B in Zong, et al.,2022) and fix the coupling holder onto the coupling box by screwing it from the outside.

Preparing the HC-920 fiber assembly

The HC-920 assembly building video tutorial can be found on the link: https://www.youtube.com/watch?v=HjAtoPbDu8E

Step11. | Cut about 2.5-meter HC-920 (item 31).
Caution! Throughout this and next steps, keep the fiber straight, always without nods, to not break or damage it.
Caution! Extra length at both ends of the fiber are added because multiple cuts are usually needed before obtaining a very flat and clean tip.
Step12. | Prepare ~ 1-meter heat shrinkage tube1 (item 7). Slide the HC-920 fiber
prepared in step11 inside the tube1. Attach tube1 with medical tape ≈10cm away from one of the ends to hold it in place for a temporary fixation.
Caution! Leave enough space (approx. 10 cm) between the top edges and the tube1 to avoid cutting the jacket if a flat tip was not obtained.
Step13. | Slide the prepared HC-920 into the Coupling protector (item 24). Add two
pieces of short heat shrinkage tubes with length of 10 cm for tube1 and 2 cm for tube2 (items 7) - see Fig. 3.
Caution! Must put the coupler protector before put shrinking tubes on.

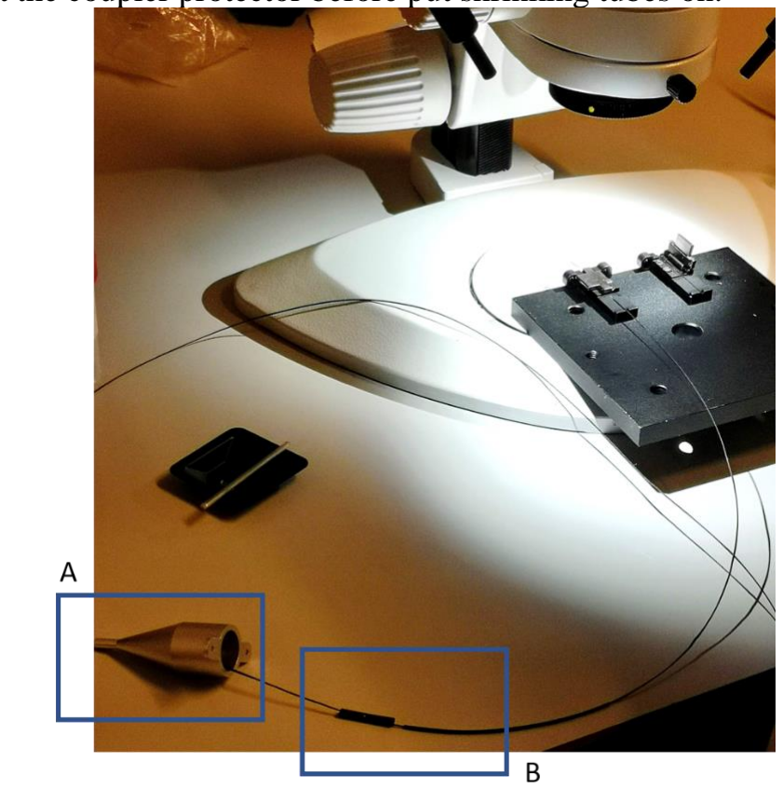
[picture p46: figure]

Figure 3: Preparation of HC-920 fiber assembly: before cutting the fiber tips (steps 15-16), slide (A) the coupling protection;
(B) heat shrinkage tubes through the HC-920 fiber.
Step14. | Prepare the other end to the collimator with three pieces of shrinking tube: 5cm
of tube1, 2cm of tube2 and 1.5cm of tube3 (see items 7). Slide them over the HC-920.
Step15. | Heat-shrink the longest jacket, tube 1 using heat gun at around 250°C. Start
from one end and hold the gun for 1-2 seconds while sliding your fingers to both ends. Caution! Handle the heat carefully – it is hot (T heat gun > 200°C)!
Caution! Avoid radiating the heat gun into fiber for too long because it can damage it.
Step16. | Remove about 2cm protecting claddings of the HC-920 on both ends by using
a fiber stripping tool (item b). Clean with a paper tissue dipped in 100% ethanol.
Step17. | Cut both ends of the fiber with the fiber cleaver (item c) based on the operating
manual provided by Thorlabs. (https://www.thorlabs.com/drawings/50b56cf6fa45ca70-9FCDC893-D86A-5263-EDF4AC19BAB469A9/XL411-Manual.pdf)
Note! About 5 mm uncladded fiber should be kept on both ends (Fig. S8A-C). Check the ending tip quality under the stereoscope (see Fig. 4). If the ending tip is not flat and clean, re-do steps 15-16.
Note! You may also need to shorten the jacket to exposure enough length of fiber on the ends.
Step18. | Slide a cleaned glass flange (item 33) on one of the prepared ends of the HC-
920 with a curved tweezer (see Fig.5-A). Stop sliding the glass flange as soon as the end of the fiber tip is slightly sticking out at the other end of the flange (see Fig.4-A).
Caution! Do not touch the tip of the fiber, as this may damage it.
Step19. | Add UV-glue using a small fiber tip (see Fig.5-B) to the funnel at the root of
the Glass Flange. Wait for the glue to flow up. Repeat until the gap between the HC-920 and the glass flange is filled with glue, then curing the UV glue with UV light.
Step20. | Prepare the other end of the fiber as in steps 17-18.

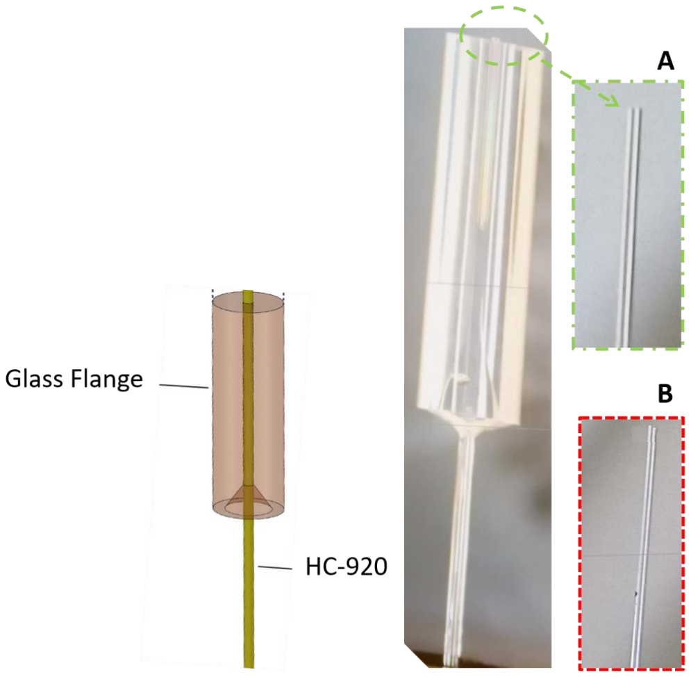
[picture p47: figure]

Figure 4: Schematic of HC-920 fiber inserted into glass flange with tip sticking out on the top side of the Glass Flange (left). Illustration of (A) a good fiber tip; (B) a bad (not flat) ending tip.

Figure 5: Assembling of a glass flange to one of the ends of the HC-920 fiber: (A) Insertion of a cleaned glass flange around the prepared end of the fiber using a curved tip tweezer; (B) gluing of the flange to the fiber by adding glue to the funnel at the root of the glass flange using a small fiber tip; (C) curing process with UV light.

Preparing the fiber collimator

The video tutorial can be found on the link: https://www.youtube.com/watch?v=HjAtoPbDu8E

Step21. | Fix the collimating lens (item 43) into the collimator holder (item 26) by using
optical adhesive (item l) (see Fig. 6)

Caution! Pay attention not to drop glue on top of the collimating lens. Also, do not use too much glue because it can flow down to the hold for the glass flange. To prevent this, flip the collimator holder and cure the adhesive on the other side as well (item e).

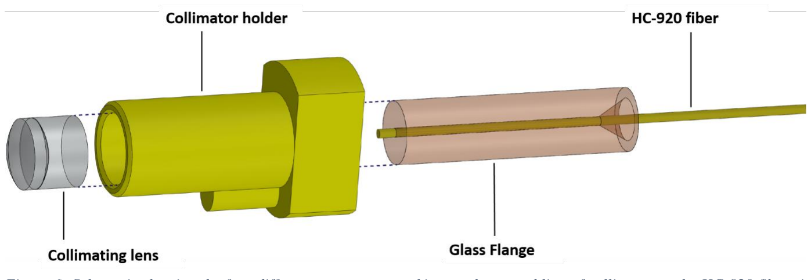
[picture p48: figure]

Figure 6: Schematic showing the four different components making up the assembling of collimator to the HC-920 fiber. A distance between the HC-920 fiber tip and collimator lens is optimized to attain collimated light when the laser beam that originates from the HC-920 fiber passes through the lens.

Step22. | Temporarily fix the collimator holder on the fiber coupling stage with
collimator assemble tool (items 10 and 25) as shown in Fig. S8E-F in Zong, et al.,2022 & Fig.7 in this document. At the same time, fix the glass flange in the clamp (item 11). Align the center of the glass flange with the center of the collimator holder, and slowly slide the glass flange into the collimator holder, by using the 3-axial adjustment on the stage (item
8) (Fig.S8E in Zong, et al.,2022).

Figure 7: Collimator holder fixated on the fiber coupling stage (left) with end of HC-920 fiber inserted in the clamp and glass flange inserted in the collimator holder. This also illustrates a section of the wider jacket (bottom right side).

Couple the laser light into HC-920 fiber (the video tutorial will be provided soon…).

Step23. | Place another fiber coupling stage in front of the coupling holder (item 11)
which is attached to the coupling box (Fig.S8D in Zong, et al.,2022 & Fig.8 in this document).

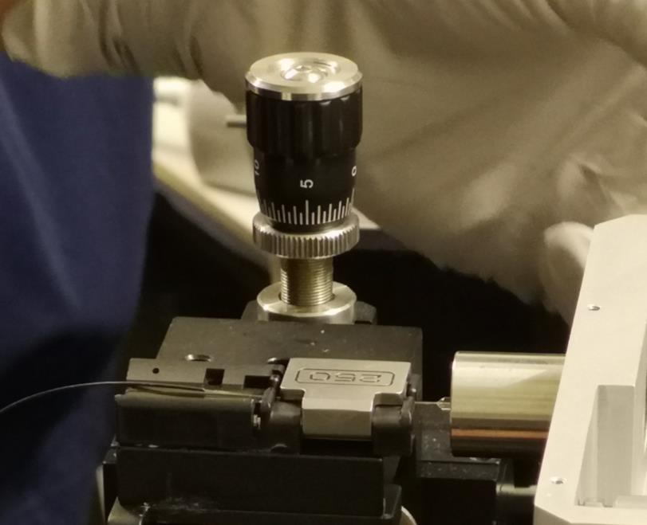
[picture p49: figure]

Figure 8: Fixation of glass flange into the clamp and insertion of the flange into the collimator holder.

Step24. | Monitor the laser power by using a power meter (item g) from the output of the
collimator. Adjust the mirror mounts in the coupling box and the distance between the glass flange and the coupling lens until the output power reaches about 70% of the input power (measured in front of the coupling lens) – see more details of this on Steps 24-25 of Laser alignment.

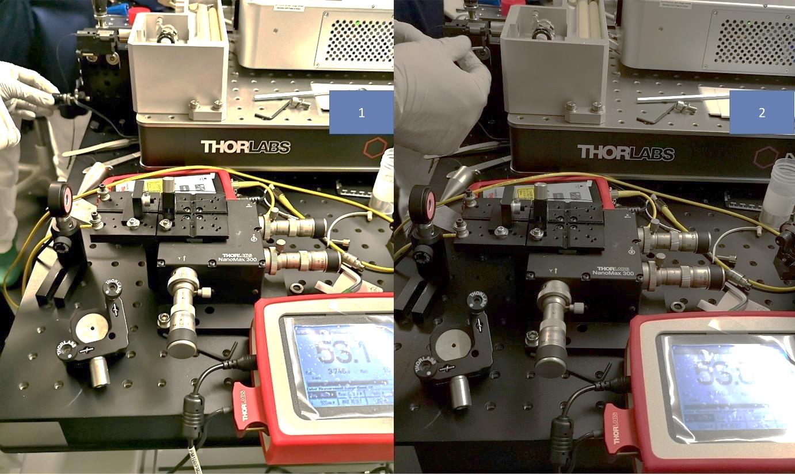
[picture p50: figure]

Figure 9: Illustration of both ends of HC-920 fiber placed on stages: first end in front of the coupling holder (top left side of both figures) and the other end aligned to the collimator holder. This figure also demonstrates the monitoring of the laser power using a power meter in front of the collimating setup. In this step, by adjustment of the distance between the glass flange and the coupling lens (Step22-1, left figure) and of the mirror mounts (Step 22-2, right figure), an ≈6% increase of power is demonstrated

Laser alignment

The video tutorial can be found on the link: https://www.youtube.com/watch?v=HjAtoPbDu8E)

Step25. | Mount SM05 threaded adapter (item 13) into stage mount (item 10). Connect
patch cable of the handheld red laser source (item f) to threaded adapter.
Step26. | Adjust the two mirror mounts (MM1, MM2 of Fig.1) of the coupling box back
and forth until both red laser (item 13) and green laser output overlap all the way to the coupling box entrance hole. Remove then handheld laser source and replace it by the photodiode power sensor (item g).
Step27. | Adjust the stage that supports the HC-920 glass flange. Slide the flange inside
the coupling holder and stop when the maximum power is reached (see Fig.9-1).
Step28. | Adjust the two mirror mounts (MM1, MM2 of Fig.1) of the coupling box back
and forth, i.e., start with one of the mirror mounts and adjust the top screw while the power increases, and stop when it decreases (see Fig.9-2). Continue with the other mirror mount, also adjust the top screw, and repeat this process to maximize the power.
Step29. | Repeat Step 27, but for the latter adjust bottom screws of both mirror mounts.
Step30. | Adjust the HWP to further maximize the output power after the HC-920 fiber.
Step31. | Glue the glass flange to the coupling holder by initially adding small amounts
of optical adhesive (item l) to cover the gap between the two. Cure it with UV light (item
c) for 60s to fixate it. Fill the gap with more adhesive and cure it again for 100s.

Step32. | Open the clamp and move the stage z-axis down, away from the fiber. Slide heat
shrinkage tube 2 (item 7) up, until it covers the glass flange, and use heat gun (item q) to shrink it. Add epoxy (item p) to the contact points.
Caution! When moving the stage down, first do this with the small cursor while monitoring the power, to make sure it is stable. When the stage is far enough from the HC-920 fiber coupling end, move it away.
Step33. | Slide the coupling protector (item 24) over and fixate it to the coupling box with
M2 screws (item t). Then slide heat shrinkage tube2 such that it enters the coupling protector and use epoxy to fixate it well to the coupling protector (see Fig. 11-1).
Step34. | Move the stage under the glass flange (collimator side) away or closer, until the
output beam is collimated (see Fig.S8-G).
Note! Check the shape of the spot at the exit of the collimator (Fig.10-A) by following the green laser beam with a NIR detector card and fixate the latter ≈2m away from the collimator. A very sharp hexagonal-star-shape spot with a gaussian-profile-like intensity distribution in the center, as show in Fig. 10-B, should be visible.

Figure 10: Laser output shining on a NIR detection card placed in front of the collimator (A) and 2m away on a nearby wall (B), confirming the light is collimated after passing through the coupled HC-920 fiber and collimator for K50-060-70; (C) output after K60-60-PM (new version of HC-920 provided by NKT fiber in 2023).

Step35. | Fixate the glass flange to the collimator holder adding small amounts of optical
adhesive (item l) and cure it for 60s.
Caution! Ensure that the laser spot described in Step31 does not change during gluing.
Step36. | Repeat Step34, adding more adhesive. Cure it for 100s.
Step37. | Slide the three thickness heat shrinkage tubes (item 7) of different thicknesses
towards the collimator holder and add epoxy to hold them: 1st tube1 to cover the fiber without the jacket; 2nd tube2 to cover the glass flange; (3rd) tube3 to cover the gap of HC-920 end and the collimator holder base (see Fig.11-2).
Note! For more details, check video tutorial HC-920 assembly, especially regarding the technique to heat shrink the three thickness tubes.
Step38. | After the epoxy is dry (overnight), remove the collimator stage.

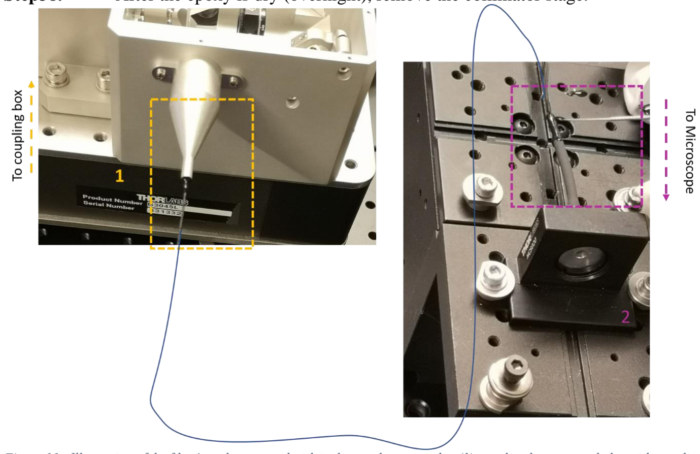
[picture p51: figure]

Figure 11: Illustration of the fiber’s ends protected with jackets and connected to (1) coupling box, covered also with coupling protection; (2) collimator holder and epoxy is placed on top to join the jackets.

Assembly of the detection module.

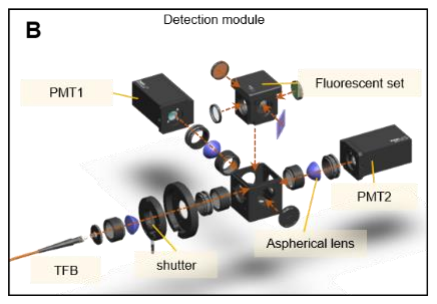
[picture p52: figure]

Taken from Fig.S7-C in Zong et al., 2022

Prepare the Cage Cube for Fluorescence Filter Sets
Step39. | Separate the removeable insert (item 14) from its base (item 15) (see Fig.S7-C
in Zong et al., 2022)
Step40. | Open the Cube Top removed on Step38 by untightening the two retaining
screws (3/32” hex) and remove half-part of the cage
Step41. | Untighten the top two screws with a Phillips #00 screwdriver to loosen the leaf
spring and slide the dichroic mirror (item 38) under the clamps (see arrows in Fig.12-A). Place the coated side of the mirror facing the direction from where the laser beam comes from. Tighten the screws enough to hold without breaking the mirror (see Fig.12-B). Caution! Do not touch the mirror, so best is to place it on the slit holding a tweezer from the corner.
Caution! To confirm which side is coated, place a tweezer with the tip very close to the mirror surface and choose the side which does not have a ghost reflection on top of the real reflection. Caution! Only light force should be applied to tighten the mirror to prevent it from moving.
Step42. | Mount back the other half of the cage and prepare the filters to assemble on the
next steps (see Fig.12-C)

Figure 12: Kinematic cage mounting steps for assembling the dichroic mirror inside the removeable cube top (A-B) and filters on the side ports (C)

Step43. | Place the cage rotated 90 degrees from its standing position with the frontside
filter port facing up.
Step44. | Remove the threaded retaining ring using either a tweezer or Spanner Wrench
2 (item d) by rotate it anti-clockwise.
Step45. | Insert the shortpass filter (item 37) with the coated side facing up and outwards,
i.e., direction of beam light.
Caution! Follow tips of Step40 to identify the coated side.
Step46. | Place the threaded retaining ring on top of the filter and with the Spanner
Wrench 2 slightly tilted, rotate it clockwise until the ring is all the way down, in contact with the filter.
Caution! Make sure there is no gap between the ring and the filter. And that the filter does not wiggle if shacked, meaning it is secure.
Step47. | Mount the 525nm and 630nm emission filters (item 35,36) on the ports as
labeled in Fig.13. For each filter, follow Steps 40-42.

Figure 13: Top view of a possible Kinematic cage configuration. The labels indicate the assignment of the filters relative to the incoming beam from the TFB. LP750 stands for 750nm lowpass filter; 525-39 and 630-69 correspond to the emission filters with centered wavelength on 525nm and 630nm with FWHM of 39nm and 69nm, respectively.

Step48. | Close the empty filter port (right side of Fig.13) with an End Cap for machining
(item 17)

Mounting TFB to kinematic cage

Step49. | Prepare a SM1 Coupler for external Threads (item 18) and place the two rotating
halfway. Attach it to the shortpass filter port.
Step50. | Thread the shutter mounting adapter (item20) to the Coupler of Step48.
Step51. | Mount the optical beam shutter (item 19) after Step49 by screwing it clockwise.
Step52. | Mount an aspherical lens (item 36) on a two connected lens tubes (item 16) and
place a threaded retaining ring on top to prevent it from moving and crash with the shutter of Step49.
Caution! The flat surface of the lens must face the TFB (outwards of cage) to collimate the beam in the direction of the kinematic cage (convergent point from the light guider to parallel laser beam rays entering the filters cage) – See Fig. 14.
Step53. | Confirm that the light coming out of Lens tube of Step51 is collimated. For this,
attach a green LED (item h) to the mount and follow visualize spot changes by approaching and distancing the assemble relative to a white wall (see Fig.15)

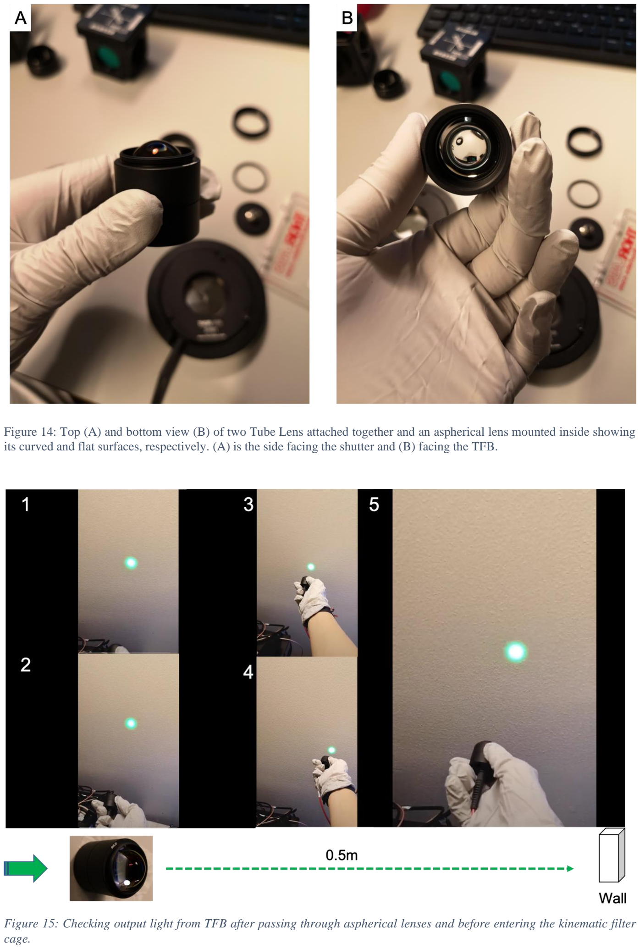
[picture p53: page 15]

Figure 14: Top (A) and bottom view (B) of two Tube Lens attached together and an aspherical lens mounted inside showing its curved and flat surfaces, respectively. (A) is the side facing the shutter and (B) facing the TFB.

Figure 15: Checking output light from TFB after passing through aspherical lenses and before entering the kinematic filter cage.

Step54. | Assemble the mounted lens on Step51 after the shutter (see Fig.16-A).
Step55. | Thread the sprayed TFB (item 30) at last.
Caution! Before adding the TFB, coat it with black rubber spray (item x) because of its grey coating. One way to ensure its uniformity is by holding it vertically and spraying very fast around 8-10x times. Wait until it dries and repeat once or twice.
Step56. | Fixate the assembled kinematic cage on top of the coupling box as shown in
Fig.16(A-B).

Figure 16: Side (A) and top view (B) of the kinematic cage connected to TFB via LP750 filter port. The cage is placed on top of the coupling´s box cap and the Tube Lenses with aspherical lenses inside are also mounted on the emission filters ports, to be connected to the PMTs (see P5.3).

Connecting PMTs to kinematic cage

Step57. | Mount another aspherical lens on Lens Tube (item 36) with flat surface facing
the PMT (outwards of kinematic cage port). Add a threaded ring to hold it in place.
Step58. | Assemble the prepared lens tube on Step56 to the Kinematic cage threading it
on the 525-emission filter port (left side – see Fig.16-B).
Step59. | Thread SM1 Coupler (item 18) to the Lens Tube with external side facing out.
Step60. | Turn off any room light. Connect PMT1 (item 52) (green channel) after coupler
of Step58. Rotate it clockwise until it is fixated. Adjust the position of the middle coupler such the PMT is in a vertical position.
Caution! When opening the PMT lid, there must not be any light source in the room to avoid damage of the PMT anode and shorten its lifetime.
Step61. | Repeat steps 56 to 59 for the 630nm emission filter port and respective PMT2
(item 52) (red channel). The result is show in Fig.17

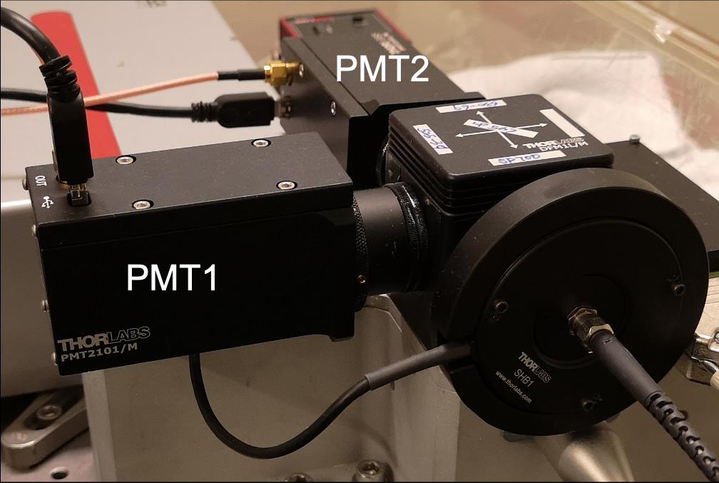
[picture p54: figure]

Figure 17: Kinematic cage connect to PMT shutter, TFB and PMTs assembled on top of the coupling box´s cap.

Mount the μTlens driver and controller for Shutter

Step62. | Fixate the Table mounting plate of the μTLens Driver (item 51) onto the core
optics breadboard (item 1), next to the Coupling box (item 21). Fixate it with two M6 cap screws (item 6), each with a washer as shown on the left side of Fig.18.

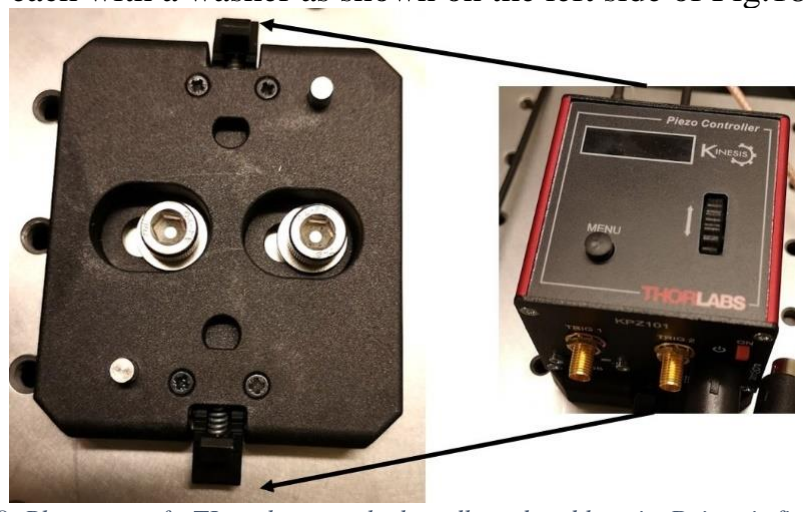
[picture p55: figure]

Figure 18: Placement of μTLens base on the breadboard and how its Driver is fixated to it.

Step63. | Mount the μTLens Driver unit on top of the magnetic plate and hold it in place
by clipping both ends inwards.
Step64. | Place the shutter controller after the μTLens Driver as shown in Fig.S7-A in
Zong et al., 2022.

Assembly of the controlling module

There are 8 input signals (BNC cables, see Fig.S9-A) connecting to the controlling box (black box in Fig.19) which then give a signal to the MEMS controller (item 44) and has as output six wires that are connected to the miniscope.

Figure 19: Illustration of the coupling box with both Input Cable from the vDAQ (left) and Output cable to the miniscope (right). An arrow on the box side indicates the direction of the signal.

Step65. | Place the MEMS controller (item 44) inside the control box shell (item 28) and
split the grey connector on the input side (connector J1) by splitting each wire.
Step66. | Attach each input DSUB15 (item 46) to the J1 connector (see Fig.S7-D in Zong
et al., 2022) to, i.e. three grounds connected to one another on the input side and to the J1 connector – Pin4 (green lines on Fig.S7-D in Zong et al., 2022).
Step67. | Link also the other pins from Input DSUB15 to J1 connector, as illustrated on
Fig.S7-D in Zong et al., 2022 (black lines).
Step68. | Connect the other side of MEMS controller to 6 pins of J2 connector. The later
then connects to 6 wires bounded with a connector, to be attached to the MEMS. This is the output signal (see Fig.S7-C, right side & Fig.S7-E in Zong et al., 2022)
Step69. | Establish direct connections from input to output, without linking to J1 or J2
connectors. This is illustrated on Fig.S7-C in Zong et al., 2022 (uTLens and LED).
Step70. | Mount the connector socket (item 48) into the backshell (item 47).
Step71. | Attach 8 BNC cables (item 95) for Signal-Input to the DSUB15.
Step72. | Repeat Step70 for output side, but merging the 6 single wire cables (item 50)
that will connect to the miniscope
Step73. | Add a 6-pin connector for MEMS (item 49) at the other end of the gathered
wires of Step67.
Step74. | Close the control box with lid (item 29).
Step75. | Mount controlling module next to the detection module, on top of coupling box
lid as shown in Fig.20 using a M4 capscrew.

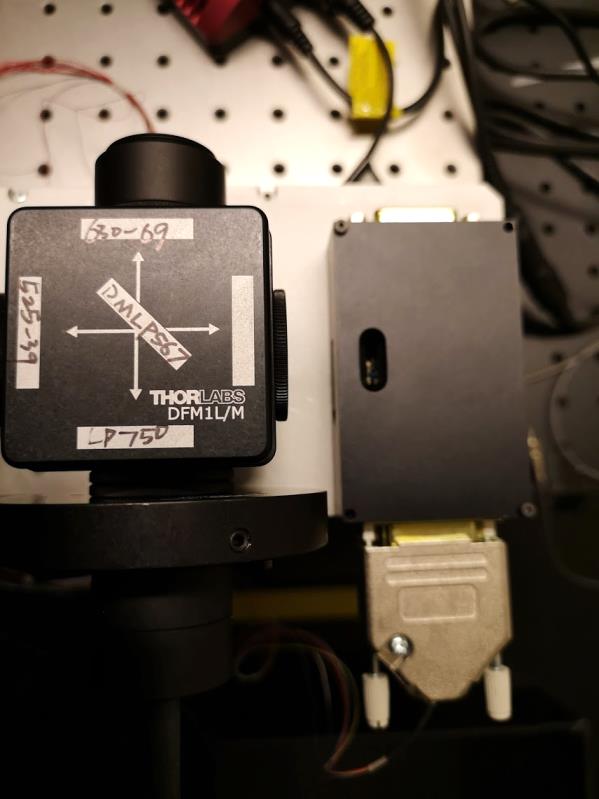
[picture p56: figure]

Figure 20: Placement of controlling module next to the detection module.

The core optics module has been successfully assembled and the result is summarized on Fig. 21.

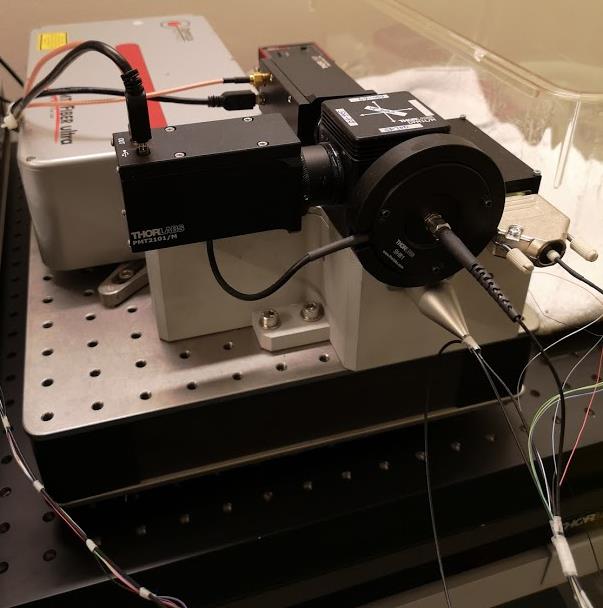
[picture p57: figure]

Figure 21: Overview of core optics module with coupling box placed in front of laser seed, detection and controlling modules assembled on top of the coupling box cap.

### Part 2- Scope Mounting Assembly

The assembling of the Scope Mounting module is divided in three parts: A) Motorized and rotatable scope holder; B) Head-fixed running Wheel; C) Illumination and Recording. This Protocol includes the main steps to build such module as illustrated in Fig.S7E in Zong et al., 2022.

Taken from Fig.S7E in Zong et al., 2022

Equipment:
- Hex keys (M2.5, M3, M4, … M6)
- Screwdrivers (Cross Slot/Phillips, Hexagon)
- Components of the Scope Holder (Table 1)
- Components of the Head-fixed Running Wheel (Table 2)
- Components of the Illumination and Recording (Table 3)

Table 1: Components of the Scope Holder setup
Component Name | Amount | Item Number (see Protocol S1)
Breadboard | 1 | 54
Sorbothane Feet | 1 | 55
Construction Rail | 1 | 56
Rail carriage | 1 | 57
Precision construction Rail | 1 | 58
Post mounting clamp | 1 | 59
Manual rotation stage | 1 | 60
MINI2P Holder P1 | 1 | 72
DC Motors | 3 | 82
MINI2P Holder P2 | 1 | 73
MINI2P Holder P3 | 1 | 74
Optical Post | 1 | 62
Base for item 58 | 1 | 61
MINI2P Holder P4 | 1 | 75
Hex Screw M2, M2.5 | 1 | 113

Table 2: Components of the Head-fixed Running Wheel
Running wheel (wheel spread + spray) | 1 | 63
Spacer1 | 2 | 64
Spacer2 | 2 | 65
Bearing | 1 | 66
Wheel Holder | 1 | 76
M6 cap screw | 1 | 6
Right-angle clamp | 1 | 67
Pillar posts | 2 | 68
Construction Rail | 1 | 56
Rail Carriage | 1 | 57
Headbar holder | 1 | 77

Table 3: Components of the Illumination and Recording setup
Universal Post Holder | 2 | 69
Zelux CMOS camera | 1 | 79
C-Mount Adapter Lens | 1 | 71
Lens 4.5 or 8.5mm focal length | 1 | 80
Locking Ball and Socket Mount | 9
LED array lights | 1 | 78
LED Power supply | 1 | 78
Basler camera | 1 | 81

Assembling of Motor Stages

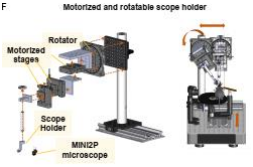
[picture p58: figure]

Taken from Fig. S7F in Zong et al., 2022

Step1. Fix the construction rail (item 56) to the breadboard (item 54) with four M6x12 mm cap screws (see Fig.22-A) and add the rail carriage on top (see Fig.22-B).

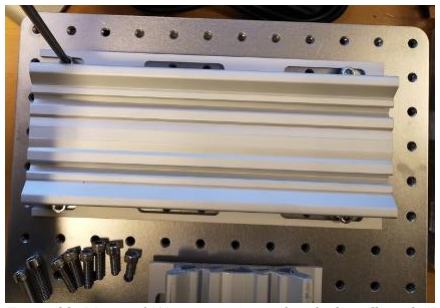
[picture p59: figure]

Figure 22: Mount of (A) construction rail to the breadboard; (B) rail carriage and mounting post on top of each previous components.

Step2. Mount all components for the scope holders on the construction rail (See Fig. S7-F in Zong et al., 2022).
Caution! Before assembling the PI motorized stages (item 82), connect the elongated cables to the Motor controller (see Fig. 23), and move the motor to one end of its range by the software to reach the screw holes.

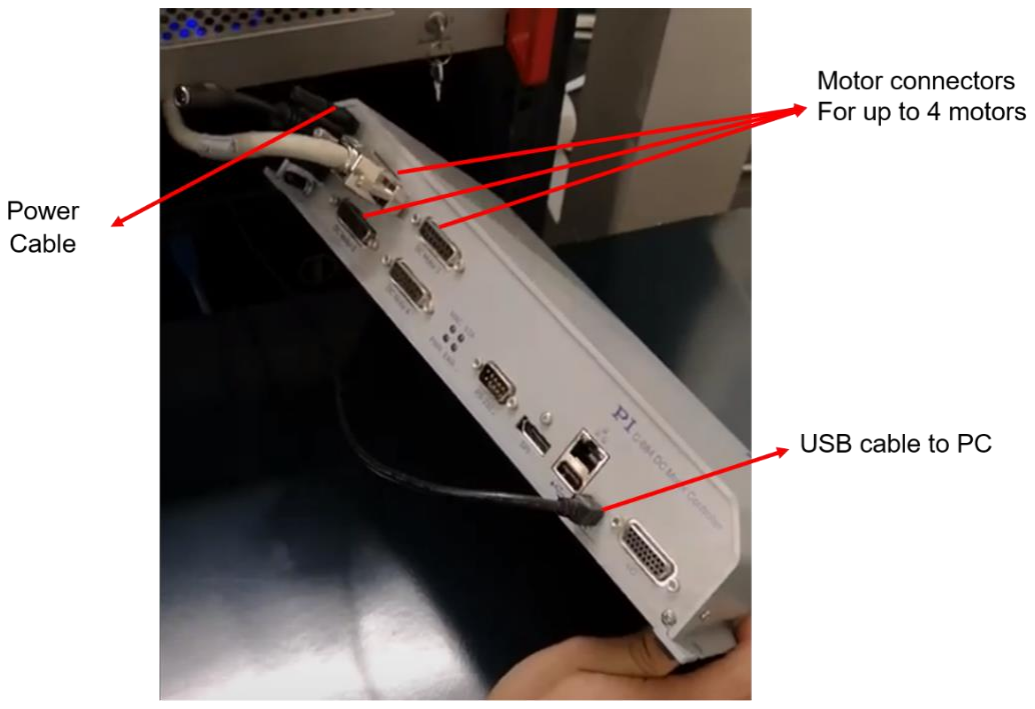
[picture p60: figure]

Figure 23: Photography of the DC Motors controller. Only one motor is connected (DC motor 1), yet this controller can allocate up to four motors.

Step3. Fix the precision construction rail (item 57) to its base (item 61). Adjust the height of the scope holder by releasing the M6 screw of the rail carriage on the precision construction rail. Adjust the angle of the scope holder with the rotator (see Fig.24)

Figure 24: Placement of MINI2P Holder P1 (item 72) relative to the manual rotation stage (item 60) and alignment of the latter to the reference line on the right. The top right figure illustrates the assembly of DC motor1(item 82) to the longer side of MINI2P Holder P1.

Figure 25: Illustration of assembling the stage (1-2), MINI2P Holder P3 (3) and MINI2P Holder P4(4).

Assembling of the Running Wheel

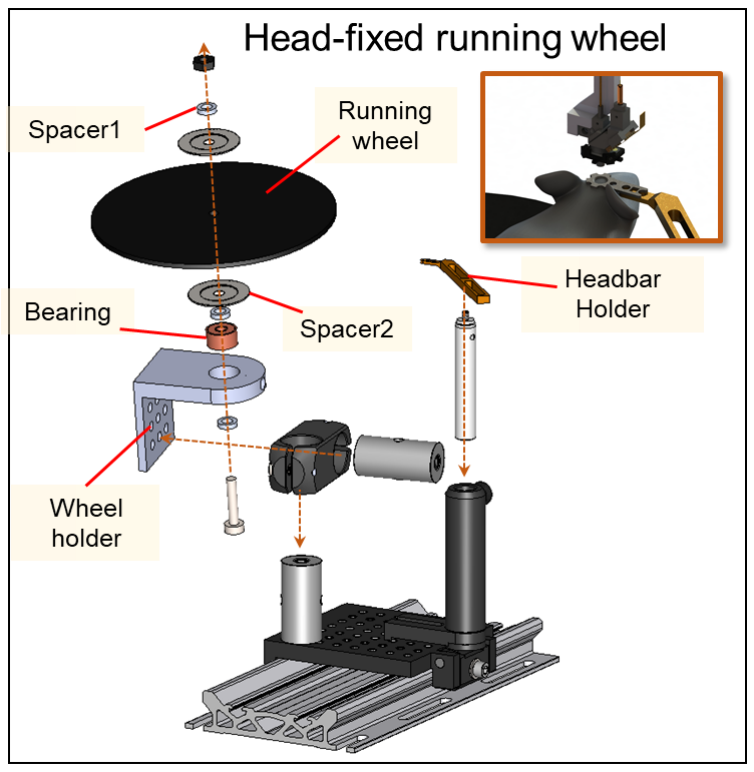
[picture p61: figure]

Taken from Fig.S7-G in Zong et al., 2022

Step4. Make the wheel spread
i. Cut hardboard (Item 80) to a circular shape (diameter Ø = 17 cm). One of the methods used can be a Jigsaw machine which is dragged in a compass-like movement to make the cut smoother (see Steps i) and ii) in Fig.26).
ii. | Create a hole for M6 screws in the center of the running wheel prepared in i. and for that, use a Drill Tower with a 6mm drill bit placed above the hardboard, as shown in Fig.27.
iii. | Spray the wheel with black rubber spray approximately ten times, until the surface is uniformly opaque black. Between spray sessions, wait ~ 10 min until it dries (see Fig.28).

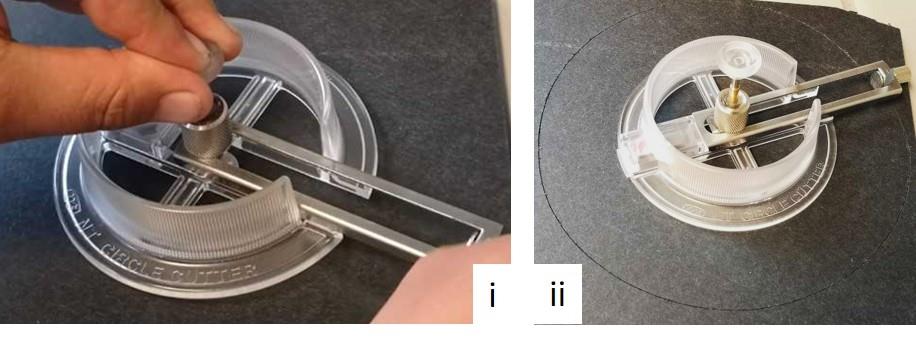
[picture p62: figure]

Figure 26: Hardboard cutting method to make a running wheel. By using a Jigsaw machine with a blade on the end-tip (i), slide it circularly with the desired diameter (in this case Ø = 17 cm) and dragging its blade, pressing the center with the fingers. Repeat one or twice until the circle is well separated from the main hardboard (ii) and then remove it.

Figure27: Illustration of process to create a hole centered on the running wheel hardboard to fit M6 screws. The circular hardboard is placed under the 6mm drill bit of a Drill Tower.

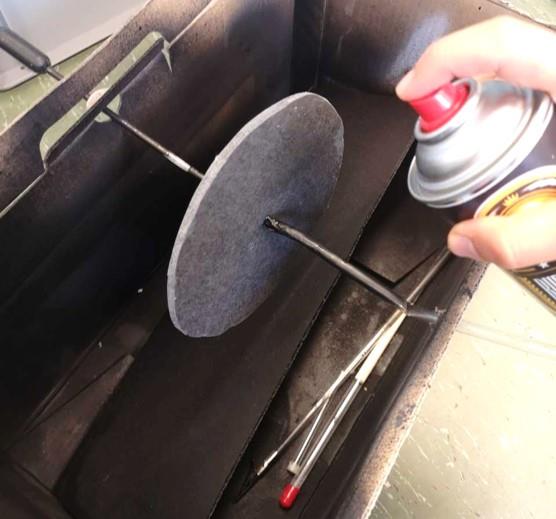
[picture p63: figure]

Figure 28: Spraying setup: a hanging wheel between two holes on opposite sides of a paper box.

Step5. Fix the other construction rail (item 56) to the breadboard and mount all components for the head-fixed running wheel on the construction rail, as illustrated on Fig.S7-G in Zong et al., 2022 and Fig.29 to Fig. 32.

Figure 29: Schematic overview showing the disposition of Running Wheel, with construction rail positioned beneath the Motors setup. The Illumination and recording stand on the side.

Figure 30: Schematic of the base to assemble the Running Wheel

Figure 31: Bearing (left) mounted on Wheel Holder (middle) and Top view of the Running Wheel before mounting the wheel itself (right).

Step6. Mount the NIR camera (item 92) and NIR LED (item 91). Adjust the positions of the camera mount and LED mounts (item 87) so the illumination and the camera focus are on the animal`s head.

Figure32: Running Wheel result.

### Part 3- Mobile Cart Assembly

The Mobile Cart Module comprises a breadboard cart which supports a drawer to store microscope objectives and other useful tools (screw drivers, spacers, clean lens tissue, swabs, etc), a rack that has a workstation (desktop computer), acquisition breadboard and controllers for both laser and DC-motors. Furthermore, it supports all the other units (Core Optics and Scope Mounting Assemblies) which are available on top of the larger breadboard. It is the basis of this setup and facilitates the transport and maneuver of the whole system, and so one can compare it to the pillars of a house: without it, the whole structure is not as strong and complete.

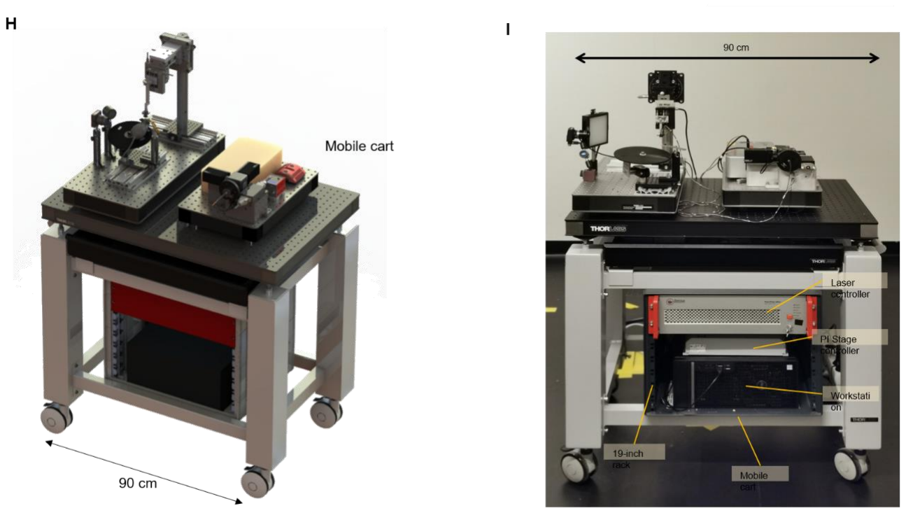
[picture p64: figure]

Taken from Fig.S7 (H,I) in Zong et al., 2022

Equipment:
- Hex keys for M4, M6 screws
- Philips screw drivers for M4
- Bubble level
- M4, M6 Cap screws
- Components of the Mobile Cart (see Table 1)
- Components for Connecting Cables (see Table 2)

Table 1: Components of the Mobile Cart
Component Name | Amount | Item Number (see Protocol S1)
Mobile Cart | 1 | 83
Main Optical breadboard | 1 | 84
Storage Drawer | 1 | 85
19-inch rack | 1 | 86
Span-In Nuts | 10 | 87
Breadboards for modules | 2 | Items 1, 54
Workstation | 1 | 88
Monitors | 2 | 89

vDAQ – acquisition card | 1 | 90
vDAQ breadboard | 1 | 91
Motion Controller for PI motors | 1 | 92
Controller for 920nm laser | 1 | 93

Table 2: Components for Connecting Cables
Controlling box
BNC cables | 8 | 95
BNC to BNC adapters | 8 | 95

µTlens controller
BNC to SMA male connector | 1 | 96
BNC adapter Female-Female | 1 | 95
SMC connector | 1 | 97
Power supply | 1 | 99

Lasers Controller
Power In Connector
USB B connection cable to workstation | 1 | Included with item 93
Ethernet | 1
D-sub15-connector to Seed Laser | 1
TTL in | 1
Analog In (SMA-connector) | 1
Trigger Out | 1
Keys for Key Switch | 1

Laser Head
AOM connector (SMA cable) | 1 | Included with item 29
Optical Fiber Input | 1
Laser Control Unit Connector | 1

PMT
USB Male A to USB 2.0 | 1 | Included with item 52
SMA to SMB cable | 1 | Included with item 52

Monitor to Workstation
HMI cable | 1
Ethernet cable | 1
USB B (screen) to USB 3.0 | 1

Workstation
USB 3.0 & 2.0 cables | 4
USB-hub (7) ports | 1 | 94
Basler power cable | 1
USB 3.0 Micro-B for Basler camera | 1

Assembling of Mobile Cart

Step1. Lock the casters to assemble the Mobile Cart (item 83) without moving it.
Step2. Mount a 19-inch Rack (item 86) following supplier instructions (see Protocol S1). Step3. Remove the frontal frame from the Mobile Cart and insert the Rack positioned on the bottom frames as shown in Fig.33-A.

Figure 33: Top view of Rack inserted into Mobile Cart (A) and Drawer mounted on top (B).

Step4. Mount the Users tools Drawer (item 85) on the mobile cart following instructions given by Thorlabs (see Protocol S1).
Step5. Add Span-In nuts (item 87) on the front and back rack’s side to later fixate Laser Controller and vDAQ breadboard, respectively (see how these are placed in Fig.S7-I) Step6. On each of the four corners of the Mobile Cart, place an adjustable anti-slip support pad aligned to each of the height adjusters. Using body weight, press the pad down until hearing a click.
Step7. Annex a breadboard (item 84) on top of the four circular adjustable mounts.
Step8. Level the mounts to minimize the breadboard tilt. Use a bubble level to adjust.
Step9. Place the two smaller breadboards (items 1 and 54) on top of breadboard mounted on Step7.
Step10. | Add Scope Mounting and Core Optics assemblies to each breadboard.
Step11. | Attach the Laser Controller (item 93) to the upper section of the front rack.
Fixate it with four M6 screws (see Fig.S7-I).
Step12. | Attach the vDAQ breadboard (item 91) to the back side of the Rack and beneath
the position of Laser Head. Insert M6 screws to the Snap-In Nuts to hold it in place.
Step13. | Place Workstation (item 88) near the bottom rack grids to maximize ventilation.
Step14. | Lay the motion controller for PI motors (item 92) on top of the workstation.

Connecting Cables / Main Connections

For more details of Steps 15-18 & Step 21, please consult vDAQ Datasheet Installation guide (https://vidriotechnologies.com/wp-content/uploads/2022/01/vDAQ-Datasheet.pdf) (see link of Items 90,91 on Protocol S1).

Step15. | Slide workstation cover and remove its second back grid as shown in Fig. 34.
Step16. | Insert acquisition card (see Fig.34-A) through the inside of the CPU with the
connectors sticking out through the open grid´s rack (see Fig.34-B1). Place it between blue and white boards and press it downwards and to the left until it clicks.
Step17. | Before closing the workstation, link the acquisition card to one of the CPU PCI
Express Power Connector (Molex connector) which is a six-pin connector as described in Datasheet Installation Guide. (https://vidriotechnologies.com/wp-content/uploads/2022/01/vDAQ-Datasheet.pdf)
Step18. | Connect the breakout breadboard to the acquisition card. For that, link two
cables from the ports of the former, labelled A and B to the top and bottom ports of the latter (see Fig.34-C and Fig.35).

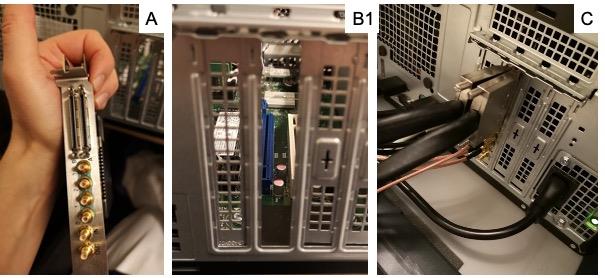
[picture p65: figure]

Figure 34: Assembling of acquisition card (A) in workstation showing front view (B1) and top view (B2) of section where the card is mounted into: on the second grid (B1), placed between the blue and white board. (C) illustrates the power cables connected from A and B channels (left and right) of the acquisition card to the vDAQ breadboard.

Figure 35: Schematic to illustrate connecting A,B - power cables to the vDAQ breadboard backside, top(A) and bottom (B)
(1) from the acquisition card (2, B-left and A-right side, as labelled).
Step19. | Connect three USB 3.0 and a USB 2.0 cables from Scope Mounting Module
monitoring camera (item 79), tracking camera (item 81) and motion controller for PI motors (item 92), respectively, to the workstation ports.

Caution! As there are not enough ports, add extra USB-hub (item 94) on top of the workstation.

Step20. | From the backside of the workstation, connect also to the monitor/screen(s):
HDMI port(s), ethernet cable and USB 3.0 to USB B.
Step21. | Link the connections shown in Fig.S9-A that go from/to vDAQ breadboard
to/from Controlling Module (Signal Input), μTLens Driver, Laser and Shutter Controllers and Tracking Camera.
Step22. | Connect also BNC7 of controlling module to HV Out of μTLens Driver (short
cable SMA to BNC). Moreover, connect the Power of the Driver on the front side. Caution! The μTLens Driver power cable has pins with specific orientation, be careful to place those pins with the correct alignment before pushing them in.
Step23. | Connect a BNC-to-BNC cable from TTL input (front side) of the Shutter
Controller to vDAQ (Digital channel D02). To this unit, link also the Power cable (5V DC, 2.4A) from the backside of the Controller.
Step24. | Finally, attach the Shutter controller to Shutter Head via the jacket next to the
Power, also backside.
Step25. | Link each PMT from its USB Port to the backside of the workstation.
Step26. | Connect the two PMTs SMA output cables (item 52) to the acquisition card
channels 0 and 1. The MINI2P system should be now completed.

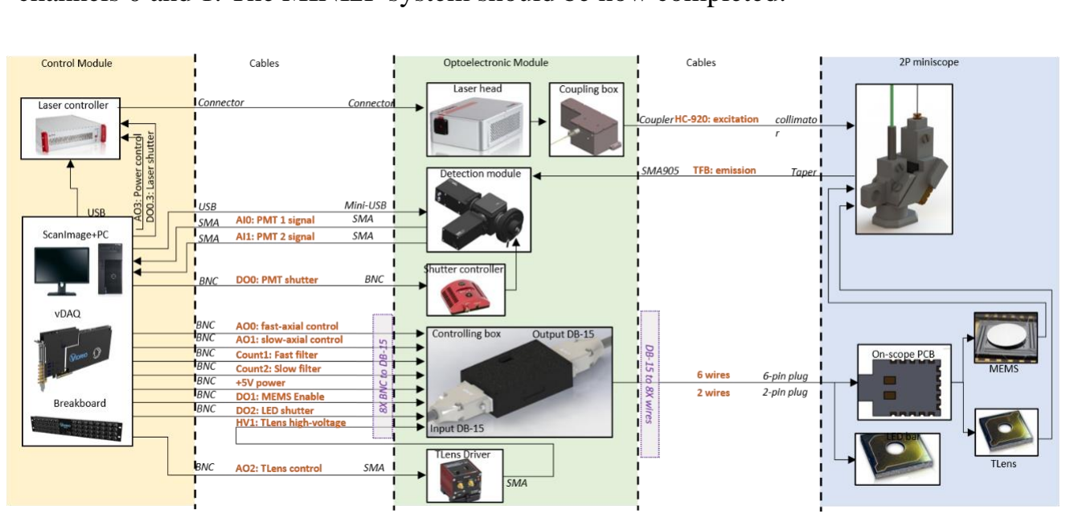
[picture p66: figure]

Taken from Fig. S9-A in Zong et al., 2022

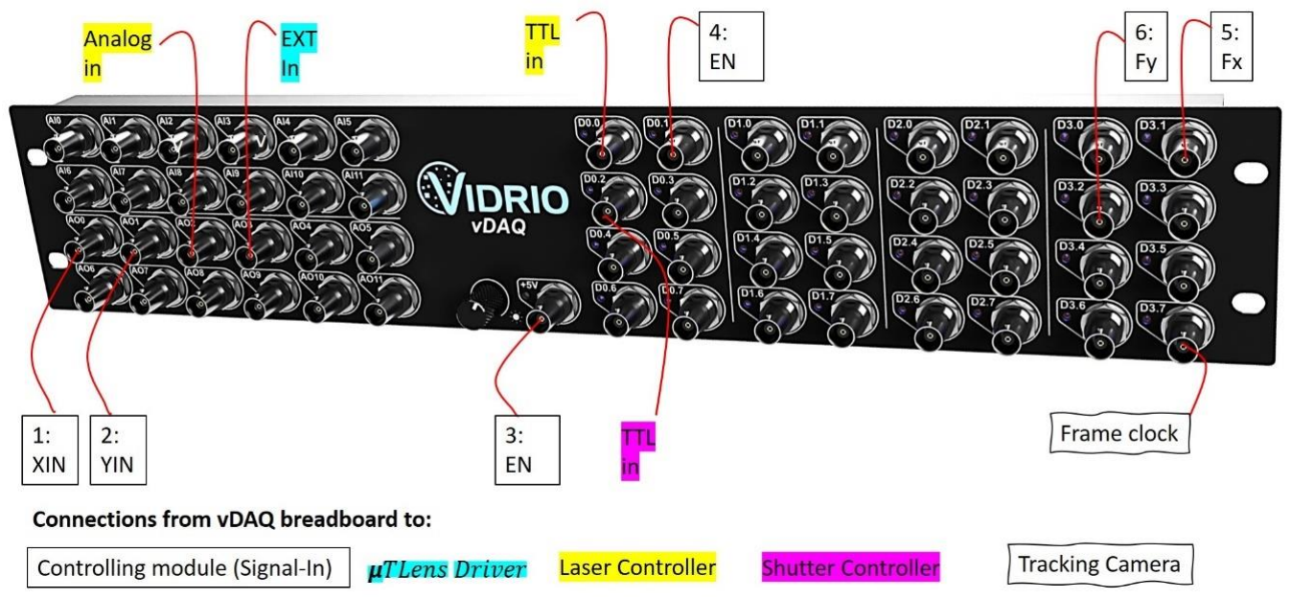
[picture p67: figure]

Figure 36: Diagram showing main connections from vDAQ breadboard to the controlling box (BNCs 1 to 6), μTLens Driver (EXT in), Laser Controller (Analog In and TTL in) and Tracking Camera (via pink BNC connector, to input-2 – see Wiki section of AnimalTracker). (https://github.com/kavli-ntnu/MINI2P_toolbox/wiki/AnimalTracker.vi)

Figure 37: Connections to the back (A) and front (B) of the μTLens Driver, as well as top view (C). HV OUT connects to BNC7 of the controlling module/box (SMC connector to BNC), whereas EXT IN is linked to the vDAQ (SMA to BNC, Analog output AO3). IMPORTANT: When connecting the piezocontroller, select HV of 75V, not higher!

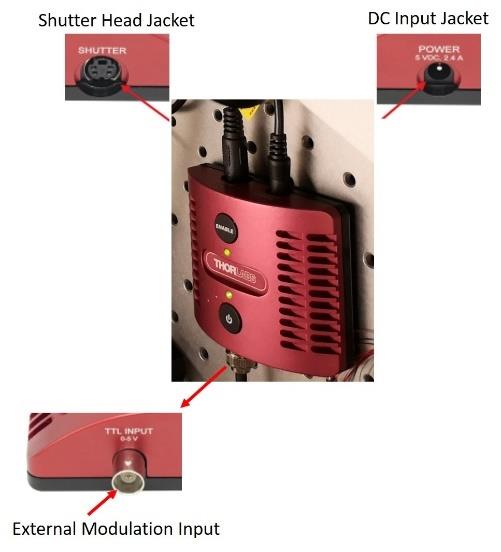
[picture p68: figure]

Figure 38: Top view of Shutter Controller with power on (bottom green LED light) and shutter opened (top green LED light right under enable button). The controller rear view (zoomed-in inlets) shows the main connections: TTL Input to the vDAQ (External Modulation Input), Sutter Head Jacket to the Shutter Head and Power (DC input jacket).

Scan Image configuration*

Controlling module | vDAQ channel | ScanImage (MDF of MEMS-L 2000Hz)
1_X «fast axis» | AO0 | Dabs.generic.GalvoPureAnalog (slow axis)* Control channel/…/AO0
2_Y «slow axis» | AO1 | Dabs.mirrorcle.ResonantAxis (fast axis)* Zoom control channel/vDAQ0/AO1 Filter clock DO channels X – D3.2 250000 Y – D3.1 100000
3 +5V | +5V
4 EN | D0.1
5 Fx «fast filter» | D3.1 | Defined in Dabs.mirrorcle.ResonantAxis
6 Fy «slow filter» | D3.2
7 TLens | HV out piezo controller
8 | - | LED not in use

Note: MDF parameters for slow and fast axes vary depending on the MEMS scanner, if MEMS-L (2000Hz) or MEMS-F (5600Hz).

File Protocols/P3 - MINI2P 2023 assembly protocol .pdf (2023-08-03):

## MINI2P 2023 – Miniscope assembly protocol

This protocol describes the assembly of the newest miniscope version, MINI2P 2023, illustrating its new features compared to MINI2P 2022. A table with useful equipment is also included. Preliminary cleaning and testing of parts, combined with the four main steps take approximately 2h to complete.

## New features in MINI2P-2023

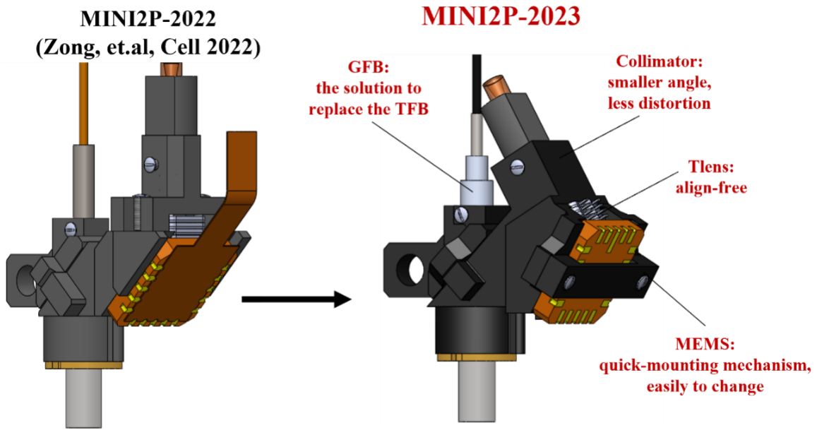
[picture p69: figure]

- A GRIN-connected fiber bundle (GFB) (https://github.com/kavli-ntnu/MINI2P_toolbox/blob/main/Protocols/GFB%20Assembly%20Protocol%20.pdf) to replace the not-available TFB;
- Small incident angle of the collimator decreases the scanning distortion;
- Tlens can be mounted in-house and it is “align-free”;
- A quick-mounting mechanism for mounting the MEMS on the scopebody; MEMS can be easily changed if broken.
- Can be assembled in 2 hours;
- 8% less weight (2.23 g now).

MINI2P 2023 assembly tutorial video can be found on the link: https://youtu.be/wqhDkIUZHgM

Check also MINI2P Video tutorial complete package: https://www.youtube.com/playlist?list=PLonWNO9SywvJXpIgQEp6jQMSh_jrn_jPU

GitHub 2D/3D models under MINI2P_toolbox/Hardware/
New P1 – Shopping Machining List 2023 under MINI2P_toolbox/Protocols/

## MINI2P 2023 key steps

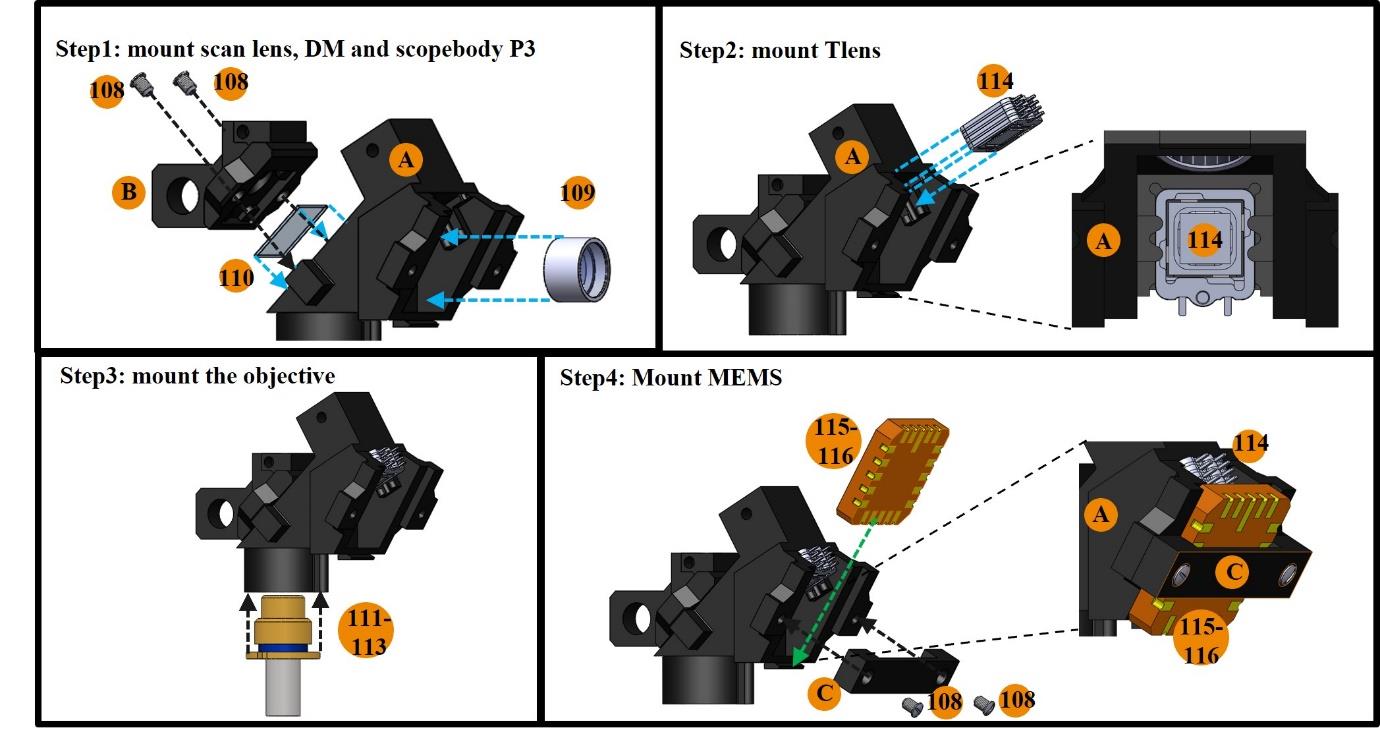
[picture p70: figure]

### Reagents and other useful equipment

Component Name | Supplier | #Item
Scopebody P1 | 3A prototype | #A102_2023
Scopebody P2 | 3A prototype | Does not exist
Scopebody P3 | 3A prototype | #B104_2023
MEMS locker | 3A prototype | #C118 (new!)
TLens testing holder | 3A prototype | #D107 (new!)
MINI2P holder P4 version 2 | Thorlabs | 75 version 2
Optical post | Thorlabs | TR75/M*
Post holders | Thorlabs | UPH75/M*
Locking ball | Thorlabs | TRB1/M*
TLens (4 stacked) | PoLight | 114
TLens connector to MEMS | Polight/LabMaker | 114
MEMS mirror (L or F) | Mirrorcle | 115/116
MEMS PCB | LabMaker | 117
MEMS connector to TLens | LabMaker/Polight | 117
Scan lens | Domlight | 109
Dichroic Mirror (DM) | Fuzhou Sunlight | 110
Objective | Domilight | 111/113
M1.2 cap screws (2 pcs) M1.4 cap screws (2 pcs) | - 108
Cotton Swabs | Chemtronics | k
Tack-It | Faber Castle
Lens cleaning tissue | Thorlabs | j
Air duster | PRF 4-44 | w
UV Adhesive glue | Thorlabs | l
UV curing gun | Thorlabs | e
Super Glue 415 | Loctive | p
Silicone Adhesive | Winjee | o

Allen keys | -
Splice protector sleeve | Thorlabs | m
Tweezers & scalpels | - | -
Ultrasonic bath | -
Medical tape | -
Handheld red laser | Thorlabs | f
Absolute ethanol | -
Unless otherwise indicated, only 1 pc needed. *Variations of these items work too.

## Preliminary steps before assembly

Prepare to mount the miniscope, but first it is recommended to both clean scopebody parts and test MEMS mirror and TLens. These steps must be done under a stereo-microscope and in a clean room.

i. Cleaning scopebody parts P1 (A102_2023) and P3 (B104_2023)
Cleaning scopebody P1 (item #A102_2023)
✓ With a scalpel, remove any chamfers sticking out.
✓ Cut surfaces where optical components will be mounted as flat as possible (Fig.1)

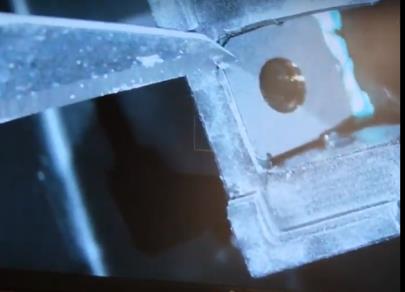
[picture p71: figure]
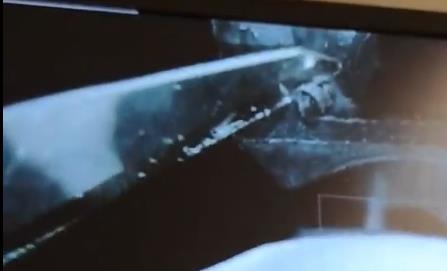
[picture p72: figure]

a) b)

Fig.1: Preparation of scopebody P1 surface to glue the MEMs onto. Cut excessive material with a blade in a single movement from the top (a) to the bottom(b). Photos of previous miniscope version, MINI2P 2022.

✓ Press with tack-it to remove any other residues, and clean scopebody P1 with a cotton swab dipped in 100% ethanol.
✓ Rinse all parts in 100% ethanol and clean them in an ultrasonic bath for 10min

ii. Testing the MEMS scanner The aim of this step is to confirm that the MEMS scanner is working. By letting the MEMS scan while directing the handheld red laser source at it, the scanning pattern is reflected in a calibration target (see Fig.2). This gives an estimation of the in-vivo FOV. ✓ Attach the MEMS scanner to the holder using tack-it. Then connect its wires. CAUTION! Make sure the power to the MEMS driver (BNC +5V) from the vDAQ to the controlbox is not connected. ✓ Connect BNC +5V ✓ Turn on the handheld red laser and adjust its holder until the light spot hits the center of the MEMS mirror (Fig.2a)

✓ Adjust the MEMS holder position until the reflected light spot hits the center of the
| calibration target axis (Fig.2b)

✓ Start the MEMS scanning using ScanImage. Select the scanning speed which is determined by pixels/line (e.g. 128 or 256) and click ”FOCUS.
CAUTION! Always start with higher zoom (e.g., 2.0) and NEVER change the zoom while scanning, i.e. click Abort, change zoom and only after click ‘FOCUS’.

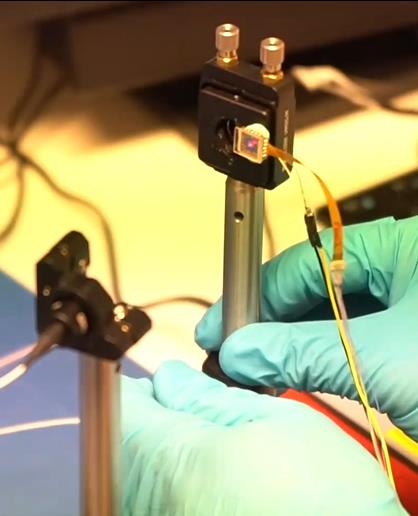
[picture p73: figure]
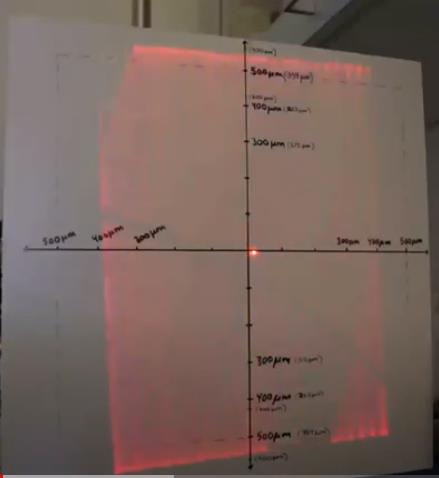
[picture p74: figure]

a) b)

Fig. 2: MEMS testing setup: red laser directed to MEMS mirror (a) and MEMS scanning pattern (b).

✓ The MEMS pattern should now appear on the calibration target (see Fig.2b).
Note! The pattern will not be square in this case because the laser is hitting the MEMS with an angle different than 45°
✓ The expected in vivo FOV is estimated by the intersection with the smallest axis. Note! In Fig.2b) can be expected a FOV of around 400 um x 400 um for Fast MEMS

iii. Testing Tlens
✓ Attach TLens to Tlens testing holder sitting on a post (Fig.3a)
✓ Insert HC-920 assembly into TLens holder`s slit
✓ Connect cable to TLens driver (piezocontroller)
| CAUTION! TLens driver must be switched off before connecting.
✓ Turn on TLens driver and scrow the knobs to enable HV.
| CAUTION! Confirm 75V is the maximum voltage range selected, otherwise it can permanently damage the TLens.

✓ Change the focal plane via ScanImage by selecting the arrows in one direction in the
| right side of “Motors Control Menu” (from 0 to - 200). Observe the change of beam profile on a NIR detection card (Fig.3b). This means the TLens works!

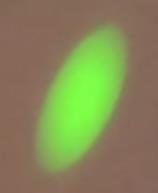
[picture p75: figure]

…

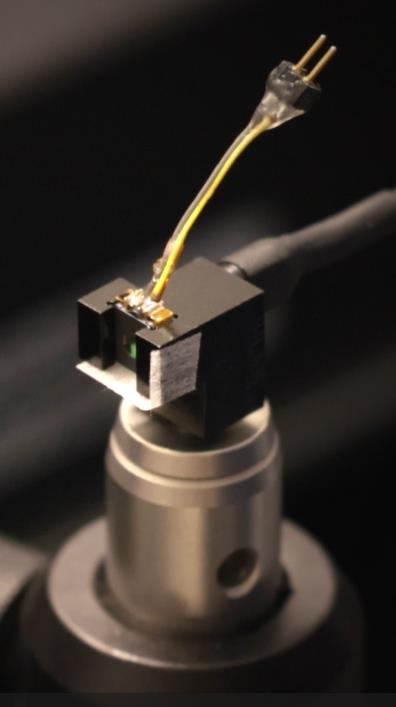
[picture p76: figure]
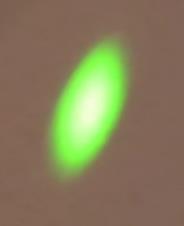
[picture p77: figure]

a) b)
Fig.3: Setup to test Tlens with HC-920 collimator holder on opposite side (a); Change of beam profile for two focal planes(b).

## Step1. Mount scan lens, dichroic mirror and scopebody P3

### 1.1 Mount the dichroic mirror (DM)

✓ Clean DM coated surface (facing down towards white paper) with lens cleaning tissue soaked in ethanol and wrapped in a cotton swab.
✓ Cut some medical tape and fixate it to the side of P1 as shown in Fig.(4a)
✓ Place the DM with coated surface facing down, slightly above the holes and leaving space for the objective on the bottom side near the collimator slit.
✓ Apply small drops of UV glue to the four corners of DM using the splice sleever (Fig.4b)
✓ Cure it with UV source while pressing the DM with the cotton swab for ≈60s
✓ Remove the tape and clean surface with a cotton swab wrapped in lens tissue soaked in 100% ethanol.

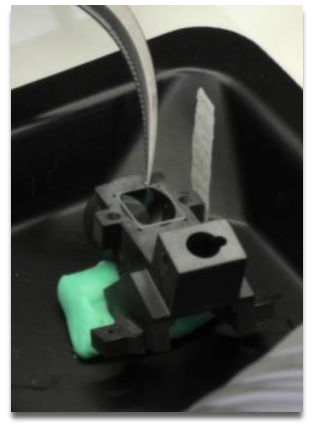
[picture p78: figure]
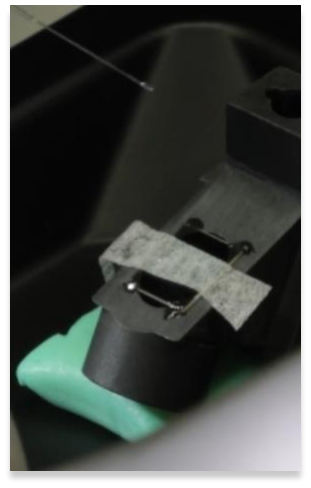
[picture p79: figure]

a) b)
Fig.4: Mounting DM with coated surface facing down: correct position (a) and fixating applying small drops of UV adhesive glue on all four corners while tape holds DM in place (b).

### 1.2 Mount scopebody P3

✓ Attach scopebody P3 to P1 to cover the DM using two M1.2 screws Tips! Screw until tight but do not force it to avoid breaking the DM.

### 1.3 Mount scan lens

CAUTION! This step must be done before mounting TLens otherwise there is no space. ✓ Grab the Scan lens around ¾ from the top with a tweezer and insert scan lens into slit.
✓ Apply small drops of UV glue in the gap around the lens with a splice sleever (Fig.5) ✓ Cure it with an UV gun for about 60s
Tips! If there are any UV drops, first cure the UV glue and only then remove it with a tweezer in a parallel direction to the lens surface to avoid scratching it.

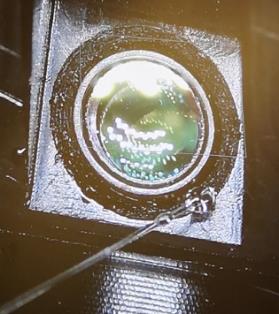
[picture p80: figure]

Fig. 5: Splice protector sleeve with a drop of UV glue being released on the gap between the miniscope and the scan lens.

## Step2. Mount Tlens

Steps 1.1 to 1.3 were similar to MINI2P 2022. However, Step 2: mounting TLens is novel and roughly “align-free”, done in-situ by the user instead of being sent to PoLight.

2.1 Gently remove protecting tapes on both sides of the stacked uTLens
2.2 Slide TLens into scopebody with coated surface facing down towards the HC-920 fiber and wires sticking outwards as in Fig.(6a). Ensure to push it all the way in as in Fig.(6b) as close as possible to the scan lens.

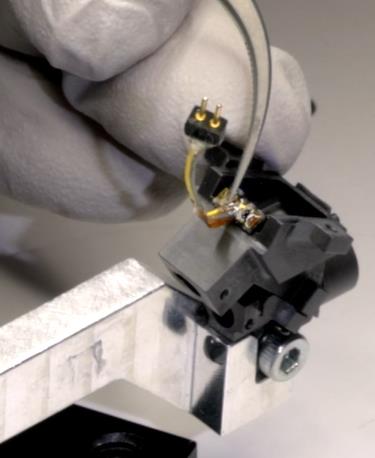
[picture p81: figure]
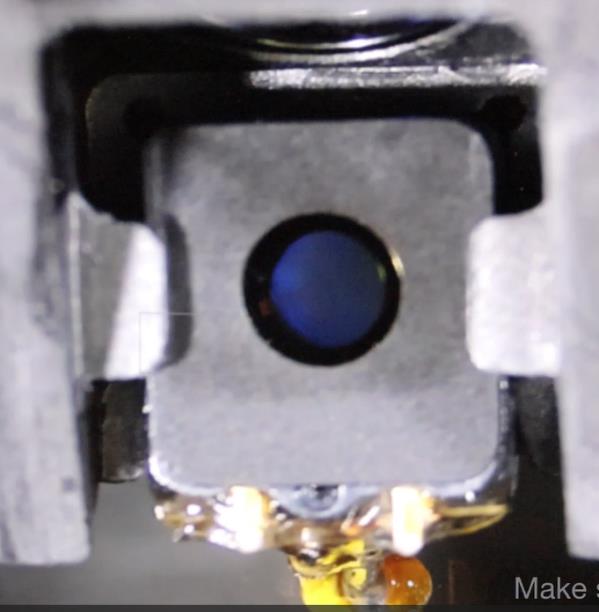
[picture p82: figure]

a) b)

Fig.6: Mounting TLens: slide TLens with coated side facing HC-920 fiber collimator (a); top view with stacked TLens pushed all the way in, as close as possible to scan lens (b).

2.3 Add small amounts of UV adhesive glue around the edges of the uTLens.
2.4 Cure with UV gun for 60s
2.5 Add small amounts of super glue near the pins to fixate it better.
2.6 Once the glue is dry, protect and shield off the uTLens.
a. Add a piece of tack-it to cover the gap to the uTlens on the top side.
b. Flatten it and attach well with the aid of a pair of tweezers.
c. Repeat a) and b) for the gap on the other side of the miniscope.

## Step3. Mount objective

✓ Screw the objective until it almost does not move.
✓ Then use a tweezer to tighten it further until there is no apparent gap between the objective and the scopebody P1.

## Step4. Mount MEMS mirror

4.1 Attach the MEMS locker with two screws without fastening them
4.2 Place the MEMS on a sticky surface with the protective glass facing down.

4.3 In a direction perpendicular to the glue, detach one side of the MEMS from the protective glass glue, then the other and lift it up.
CAUTION! This step should be done very quickly (< 15s) or under a fume hood 4.4 Slide MEMS in between scopebody P1 and locker and fix the screws.
4.5 Cover the upper space between the MEMS and scopebody, sealing the TLens gap (Fig.6a) with tack-it
4.6 Attach the Tlens wires to the MEMS, matching wires colour (black to black and yellow to yellow), and connect the MEMS flex cable (PCB) to the 6-wires (black end facing clip)
CAUTION! Ensure TLens driver is switched off and +5V is not connected. CAUTION! Ensure +5V BNC is not connected.
4.7 Power control box (+5V BNC vDAQ) and piezocontroller (activating HV)
4.8 Insert the HC-920 collimator into the scope. In ScaImage, open the laser shutter and increase power to 20%
4.9 Slightly loosen the screws of the MEMS brackets and adjust the MEMS position until the outgoing laser spot is completely circular and not trimmed (Fig. 7b).

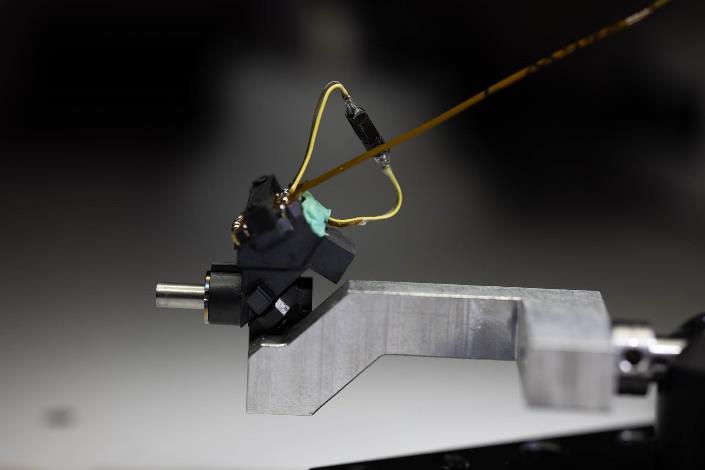
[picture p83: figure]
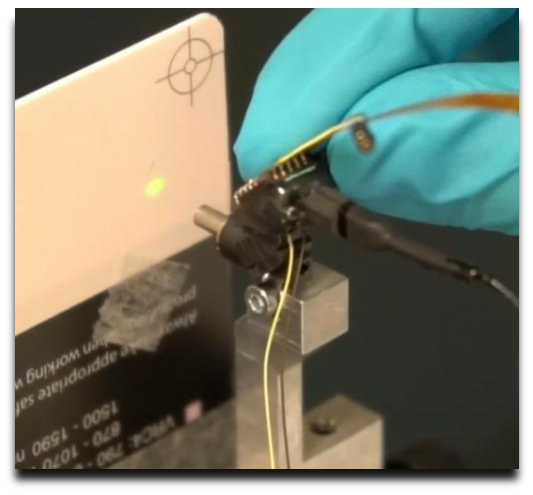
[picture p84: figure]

a) b)

Fig.7: Illustration showing the μTLens slit covered with Tack-it (a); finding optimal MEMS position with a Gaussian output, not cut (b).

4.10 Apply a thin layer of super glue along the edges of the MEMS scanner along between the MEMS and miniscope
4.11 | Leave it to dry for 5min
4.12 | Add silicone covering the entire visible parts of the MEMS in front (Fig.8a) and
back (Fig.8b)


a) b)

Fig. 8.: Finished miniscope after mounting MEMS into Scopebody P1 and covering it with silicone: front (a) and back views (b).

Tips to replace MEMS mirror when necessary to swap by another type and/or it is damaged:
✓ Start by removing the whole coverage of silicone glue with a tweezer and scalpel ✓ Insert the scalpel blade in the bottom surface to open a gap between the MEMS mirror and the scopebody P1. Force it to slowly detach each side
✓ Then push the MEMS holding simultaneously the main body and PCB in one movement.
✓ Clear all remaining glues after removed MEMS.

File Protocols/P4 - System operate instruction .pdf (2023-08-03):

## P4 - System operate instruction

## Part1: Software needed to be installed

Table1: Overview of Software needed in MINI2P Platform (updated version Jan2022)

Software | version | company | Source | License (Y/N)
MATLAB | 2019b or newer (https://www.mathworks.com/) | Mathworks | | Y
LabVIEW | 2021 or newer (https://www.ni.com/en-no/support/downloads/software-products/download.labview.html#411240) | National Instruments | | Y
PI Software Suite | PIMikroMove 1.0.7.2 (https://www.physikinstrumente.com/en/) | Physik Instrumente | CD | N
ScanImage | Basic 2021 (https://vidriotechnologies.com/scanimage/) or newer | Vidrio | | Y
TOPAS | FemtoFiber Ultra 920 (https://www.toptica.com/products/psfs-fiber-lasers/femtofiber-ultra/femtofiber-ultra-920/) | Toptica | USB flash drive | N
PulseLink | APE pulseLink (https://www.ape-berlin.de/en/autocorrelator/pulsecheck/) | A-P-E | .exe | N
PMT2100 | latest (https://www.thorlabs.com/software_pages/viewsoftwarepage.cfm?code=PMT) | Thorlabs | .exe | N
ThorCam | latest (https://www.thorlabs.com/software_pages/viewsoftwarepage.cfm?code=ThorCam) | Thorlabs | .exe | N
Fiji | Imagej (https://imagej.net/software/fiji/downloads) | Imagej | .exe | N
Pylon | Pylon 6 (https://www.baslerweb.com/en/sales-support/downloads/software-downloads/runtime-pylon-6-2-0-windows/) or newer mp4 package (https://www.baslerweb.com/en/sales-support/downloads/software-downloads/pylon-supplementary-package-for-mpeg4-windows/) | Pylon | .exe | N
MINI2P Distortion Cleaner | DistortionCleaner (https://github.com/kavli-ntnu/MINI2P_toolbox/tree/main/Analysis/Applications/DistortionCleaner) | Kavli NTNU | .exe | N
MINI2P SI device | Distortion app (https://github.com/kavli-ntnu/MINI2P_toolbox/tree/main/Software/MINI2P%20SI%20Device) (plugin app) | Kavli NTNU | | N

Guidelines

Step1. Start by installing MATLAB and LabVIEW that are needed to run the MINI2P control software ScanImage, widely used in laser scanning microscopies.
MATLAB: Install 2019b or a newer version. This requires a MATLAB license. LabVIEW: Install 2020 SP1 including the packages below. NI-DAQmx
- NI-VISA
- PXI Platform Service
- FlexRIO for Modular I/O
- FlexRIO for Integrated I/O
- NI-IMAQ
- NI-IMAQdx
Please deselect all additional items.
Note! For more information on the NI-IMAQ and NI-IMAQdx versions, please check the supported versions with the operating system provided by National Instruments in the link:

https://www.ni.com/en-no/support/documentation/compatibility/17/vision-acquisition-software--vas--ni-imaq-ni-imaqdx-ni-imaqi-o-a.html (https://www.ni.com/en-no/support/documentation/compatibility/17/vision-acquisition-software--vas--ni-imaq-ni-imaqdx-ni-imaqi-o-a.html)

Step2. Download and install the imaging control software, ScanImage Basic-2021 or newer, available in your Vidrio account after purchase (see link in Table1). Install also RDI drivers and possibly update vDAQ Firmware. Follow more instructions provided in https://vidriotechnologies.com/drivers

Step3. Install the software that runs controller of the DC motors, an executable file PISoftwareSuite provided in a CD by Physik Instrumente.
Step4. Connect the controller (item 91). For this, run the controller PIMikroMove program. Then connect to the correct controller by choosing C-884 in the USB tab. Click connect. Step5. The next step is to reference the three DC motors (item 82). For that, identify the three linear stages M-112.2DG (item 82) as motors 1 to 3 (physically confirm they connected with that attribution in the back panel of the controller). Click reference and wait for the motors to move all the way, away from the motor’s cable. Finally click done, and when closing, save the settings to avoid having to reference the DC motors again.
Caution! Before referencing the motors, confirm there is no object on the way that can crash against. Otherwise, click stop while referencing.

Step6. Installation and connection of laser control software, FemtoFiber Ultra 920 (item 29 & 93)
The laser can be connected to the workstation via USB. To install the USB drivers, follow point 5.2 of FemtoFiber Ultra 920 manual. To install the laser control software, TOPAS FemtoFiber Ultra, follow point 5.3 of the same manual. Finally, to connect for the first time, follow the manual’s point 5.4.

Step7. Install the autocorrelator software that measures the pulse width, PulseLink Check by running the executable file provided by APE (See link on Table 1)

Step8. Installation of the light detectors software, Photomultiplier Tubes (PMTs), PMT2100. Read Chapter 6 of PMT2100 Series Photomultiplier Tubes User Guide. For installation of the detector software PMT2100, follow steps 6.1 to 6.2, possibly 6.3.
Step9. Start-up the detector software PMT2100 and for both detectors, PMT1 and PMT2, type the respective serial numbers that are printed on the side of the detector, and click OK.
Step10. | Install the software (ThorCam, see link in Table 1) of the camera used to
monitor the miniscope while moving its motorized scope holder (item 79). Read the user manual, more specifically chapter 3 and follow its installation guidelines.
Step11. | Copy the folder SI settings provided in GitHub MINI2P/toolbox to your local
drive so you can fetch it later when running ScanImage via MATLAB (see step 14).
Step12. | To finish the installation part, also install the remaining software easily by
downloading and running the .exe files (See links in Table 1)
- Fiji for reading and processing data in format of .tiff
- Pylon, the software that communicates with the Basler camera (item XX) for animal tracking. Install also the .mp4 package to save the videos in that format.
- MINI2P Distortion Cleaner that runs in MATLAB to find Transformation Matrices and calculate FOV (see more in Protocol P5 – Standard Testing Protocol)

## Part2: Instructions to start-up ScanImage

More information and details can be found in: https://docs.scanimage.org/Configuration/index.html

Step13. | Run the MATLAB version installed. To the MATLAB directory, click SET
PATH to add the necessary packages. Firstly, the ScanImage folder which can typically be found in the computer hardrive, as C:\Program Files\Vidrio, and MATLAB toolbox folder.
Step14. | Start the imaging control software, ScanImage.
Type ‘scanimage’ on MATLAB command window. A ScanImage dialogue window will pop-up. Upload your license or login and select it.
Then, also select a Machine Data File (MDF) and User Configuration file. Each file is provided in Github: MINI2P toolbox/Software/SI settings. Click “Start ScanImage” (See Fig.1-top).
Step15. | Wait for SI to load. In the meantime, minimize or move MATLAB/SI window
to be able to visualize a display that enable the DC motors connector. Click on the USB tab, select C-884 +SerialNumber > Click OK (See Fig.1-bottom).
Step16. | If loaded correctly, the display should look like Fig2.


Figure 1: ScanImage starting dialogue windows with MATLAB command window on the background.

Test Laser and Calibration of Laser Look-Up-Table (LUT)

To change laser voltage in the following steps, click View> vDAQ Testpanel. Modify the voltage of the Analog Output channel that is connected to the laser by introducing its voltage, and clicking Set.

Step1. Run APE Pulse Link when the laser is aligned to the Autocorrelator (item q). Compare the Pulse Width @ 5V to the technical report provided by Toptica. Also measure the output power with power meter which has a suitable range (> 1.2W) Step2. Update the laser LUT given in AOM.beamlut file. That Table has a set of datapoints [ laser power/ P_max@2V, voltage], with values ranging from 0 to 1.0 and voltage from 0 to 2.0, in steps of 0.2, as:
[0, 0;
0.015, 0.2;
[0.054, 0.4;
…
[1.0, 2.0].
The “power” here varies between 0 and 1 because its value is divided normalized by the maximum measured power at 2V. For example, 159mW @2V, then the last datapoint of the table is [1.0, 2.0]. Nevertheless, measure the power after the miniscope’s objective with the power meter’s sensor (item g) and repeat this for all datapoints.

Step3. Set up the PMT2100 offset (see point 6.5 of Manual).

## Part3: Start up Imaging & Recording

Step4. | Mount the miniscope by screwing a M2.5 onto the Scope Holder (item 75)
Step5. | Open the control software to the camera ThorCam software and click > Capture
(camera software to monitor/visualize ) purpose
Step6. Start the laser control software TOPAS, and click Connect. Turn on Laser and wait until Power stabilizes at ~ 1200mW (a couple of minutes)
Step7. Open PMT2100 software, check if Serial Numbers match the PMTs in the OPEN2MINI system, then click ok.
Caution! Never start the PMT (meaning click play, increase gain) when the lights of the laboratory are on.
Step8. Repeat step 11 to start ScanImage.
Note! It typically shows the previous MDF and User settings used, so if this is not the first time, then confirm this is correct and click Start.
Note! A window overview should appear as in Fig. 3 of Overview Documents (dependent on the user configuration selected)
Step9. Approach the miniscope to the target focus point yet guarantee the objective does not crash against anything on the way. While moving the scope holder down with Z-Motor, use the software opened in Step11 to better visualize the proximity to the object.
Step10. | Click Focus on the Main Controls to visualize the Channel display of the FOV.
Step11. | Move z until the image is in focus and optimize the (x,y) position.
Step12. | On Main Controls, click Grab to record a FOV image. Before that, do not forget
to check Save (see Fig.2)


Figure2: Datalogging on Main Controls of Scan Image.

Step13. After finishing recording, run Fiji and drag the .tiff to check just-saved data

Preliminary tests
There are two main phases to go through before acquiring calcium imaging data, so that the MINI2P system is ready for final usage.

First, a quick check of FOV. One can optimize collimator position (and TFB/GFB) to maximize uniformity of the light, mostly in the center and edges. Secondly, laser calibration as shown in Step2. It is also advised to optimize the MEMS fast and slow axis using MDF files, but do not go above the maximum allowed voltage.

Now the user is ready to initiate the Standard Performance tests provided in the next protocol.

Quick Check to see if the miniscope is working

Step1. Prepare a Fluorescent sample: Cover a Lens Cleaning Tissue (item j) with Fluorescent Marker, painting uniformly thin rows. Place it beneath the miniscope.
Step2. Repeat Steps 19-24 until an image like in Fig.3 is visualized


Figure3: Image of Fluorescent sample to efficiently test a miniscope before, for instance, in -vivo imaging.

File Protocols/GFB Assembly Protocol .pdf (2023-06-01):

## GFB Assembly Protocol

This document describes the protocol for assembling the GRIN-end fiber bundle (GFB), which replaces the tapered fiber bundle (TFB) as the main fiber collecting and relaying the emission signal to the detection module. Please source the parts and reagents below from their respective suppliers and follow the steps below. All five steps take approximately 30min.

Note: A video tutorial will also be available at KISN Youtube channel shortly.

### Overview of steps:


### Reagents and parts:

Component Name | Supplier | Amount | Item #
Fiber bundle XMLG, Part number 1840314 | SCHOTT | 1 | 30.1
AR window dia1.8x0.2mm,S1:HT T>99%@450-700nm, AOI=0deg | Fuzhou Sunlight | 2 | 30.2
GRIN lens #64-520 | Edmund Optics | 1 | 30.3
GFB holder* | 3A prototype | 1 | 30.4
Scopebody P3 V2* | 3A prototype | 1 | 104.2
Silicone glue | RTV | 1 | o
Air duster | PRF 4-44 | 1 | w
UV adhesive glue | Thorlabs | 1 | l
UV curing gun | Thorlabs | 1 | e
Absolute ethanol | - | 1 | -
Lens paper tissue | Thorlabs | 1 | j
Tack-It adhesive (green) | Faber Castell | 1 | -
Scissors/tweezers | Elfa Distralec | 1-3 | y
Green LED LED driver | Thorlabs | 1 | h.

*2D and 3D models are available under: https://github.com/kavli-ntnu/MINI2P_toolbox/tree/main/Hardware/GFB

Step 1: Test efficiency of fiber bundle
Step 2: Glue GRIN lens to holder
Step 3: Glue AR coating to GRIN lens
Step 4: Glue fiber end to holder
Step 5: Glue AR coating to fiber end with SMA adapter

### Step 1: Test efficiency of fiber bundle

1.1 Adjust LED power output to 30 mW – this is the reference power output to measure transmission efficiency of the fiber bundle
1.2 Connect fiber bundle SMA adapter to LED output and measure power at fiber tip – 25 / 30 mW = 83 %
Note: approx. >75% transmission efficiency is acceptable.
Note: Ensure the fiber is elongated. Transmission maybe lower if the fiber is twisted.
1.3 Secure fiber bundle under the scope and observe the face of the fiber bundle under minimum LED output
1.4 Count the number of dead cores
Note: <3 dead cores are acceptable, ≥4 is not recommended (see Figs. 1-2).


Figure 1, Example of face of the fiber bundle as seen from the inside of P3 under the microscope with 0 dead cores.


Figure 2, Example of face of the fiber bundle as seen from the inside of P3 under the microscope with 2 dead cores (red arrow).

### Step 2: Glue GRIN lens to holder

2.1 Clean GFB holder and P3 by placing in 100% ethanol and sonicating for 5 mins 2.2 Dry the GFB holder and P3 using lens paper and air duster
2.3 Secure GFB holder with sticky tac under the scope, larger end facing up
2.4 Carefully place the GRIN lens inside – the orientation is not relevant
2.5 Apply UV glue around the rim of the holder and cure with UV light for at least 1 min

### Step 3: Glue AR coating to GRIN lens

3.1 Clean dust off GRIN lens with 100% ethanol-soaked lens paper
3.2 Add a small drop of UV glue on the face of the GRIN lens
Note: Too much glue may overflow onto the coating, while too little may leave air bubble
3.3 Place the coating on the GRIN lens and gently position it at the center using forceps Important: Orientation of the coating is critical.
S1 surface is the coating and should be placed on the GRIN lens to face the air. S2 surface faces the GRIN lens (Tip, S1 surface faces down on the packaging. Flip upside down and place on the GRIN lens so that S1 surface faces the air)

3.4 Cure with UV light for at least 1 min.
3.5 Clean surface of the coating with 100% ethanol-soaked lens paper

### Step 4: Glue fiber end to holder

4.1 Insert GFB holder with GRIN lens into P3
Note: When viewed from inside of P3, the GRIN lens should stick out of the P3. This ensures that the GRIN lens is all the way inside of P3.
4.2 Secure the GFB holder using the P3 as an anchor. The smaller end of the holder should face up 4.3 Add a few drops of glue into the cylindrical cavity of the holder
Note: Make sure there’s enough glue to cover the face of the GRIN lens and walls of the holder, and that there are no bubbles inside
4.4 Clean the fiber tip with a cotton swab
4.5 Insert fiber tip into the cavity, and gently move it up down to remove any bubbles
4.6 While holding it down, cure with UV light immediately
Note: Its important to ensure that the face of the fiber tip is touching the grin lens
4.7 Pull the jacket of the fiber over the metal sleeve and secure with superglue
4.8 Cover the metal sleeve with silicone glue for extra security (superglue alone is not sufficient) 4.9 Flip P3 upside down and shine UV light from the inside to ensure any residual UV glue on the inside is cured
Note: this step is to cure the glue between the inner surface of the GRIN lens and the end of the fiber bundle.

### Step 5: Glue AR coating to fiber end with SMA adapter

5.1 Clean the tip of SMA adapter with 100% ethanol
5.2 Add a small drop of UV glue
5.3 Place the AR coating with S1 surface facing the air (S2 surface faces the SMA adapter) Important: Orientation of the coating is critical.
5.4 Cure with UV light for at least 1 min

Final check: Connect the LED and observe the fiber tip from the inside of P3 under the scope. The face of the fiber bundle should be visible, with no visible air bubbles.


Figure 3, Face of the fiber bundle as seen from the inside of P3 under the scope once all the steps have been completed.


Figure 4, Example of light guide with multiple areas with dead cores. Also note the collection efficiency was under 50%.

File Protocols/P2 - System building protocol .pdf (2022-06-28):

## P2– System building protocol

### Part 1- Core Optics Assembly

Reagents:
- Super glue (Loctive, 415)
- Epoxy adhesive (item p)
- 100% alcohol
- Air duster Green (item w)
- UV curing optical Adhesive (item l)
- Rubber spray (black, item x)

Equipment:
- 2 Tweezers (preferably one flat & one curved)
- Splice Protector Sleeve (item m)
- Lens cleaning tissue (item j)
- Cotton buds & swabs for electronics (item k)
- Heat shrinkage tubings (black, item 7)
- Heat gun (item q)
- Hollow-core 920 nm fiber (HC-920) ≈ 2.5m (item 31)
- Screwdrivers
- Stereomicroscope (Zeiss Trino, WL37166)
- UV curing LED system (item e)
- Components of the coupling module (Table1)
- Components of the fiber coupling setup (Table 2)
- Components of the fiber collimating setup (Table 3)
- Components of the laser alignment (Table 4)
- Components of the detection module (Table 5)
- Components of the controlling module (Table 6)

Table 1: Components of the coupling module
Component Name | Amount | Item Number (see S1, shopping list)
Breadboard | 1 | 1
Sorbothane Feet | 1 | 2
Seed laser | 1 | 29
Coupling box | 1 | 21
Coupling box cap | 1 | 22
Glass rods | 3 | 32
Prisms | 8 | 34
Rotation mount | 1 | 5
Half-wave plate (HWP) | 1 | 41
Adjustable mirror mounts | 2 | 4
Protected silver mirrors | 2 | 42
Cap screws | 4 | 6

Coupling protection | 1 | 24

Table 2: Components of the fiber coupling setup
Coupling holder | 1 | 23
Coupling lenses | 1 | 40
Glass Flange | 1 | 33
Spanner Wrench 1 | 1 | a
XYZ translation stage & right-angle bracket | 1 | 9
Fiber clamp | 1 | 11
Pulse check Autocorrelator | 1 | r
Base to fixate Autocorrelator to Breadboard | 1 | s

Table 3: Components of the fiber collimating setup
3 axis microblock stage | 1 | 8
Fiber Clamp | 1 | 11
Glass Flange | 1 | 33
Fiber stripping tool | 1 | b
Collimator Holder | 1 | 26
Collimating Lenses | 1 | 43
Collimator assemble tool | 1 | 25
Fiber Cleaver | 1 | c

Table 4: Components of the laser alignment
Handheld laser source (635nm) | 1 | f
SM05 threaded adapter to laser source | 1 | 13
Power and energy meter | 1 | g

Table 5: Components of the detection module
Kinematic cage cube | 1 | 14
Kinematic cage cube base | 1 | 15
Emission filter 525 nm green channel | 1 | 35
Emission filter 630 nm red channel | 1 | 36
Shortpass filter | 1 | 37
Dichroic Mirror | 1 | 38
Lens Tubes | 4 | 16
End cap for machining | 1 | 17
Spanner Wrench 2 | 1 | d
Coupler | 3 | 18
Optical beam shutter with controller for PMT | 1 | 19
Post mounting adapter | 1 | 20
Green LED | 1 | h
Aspheric Condenser Lens | 3 | 39
μTlens driver | 1 | 51
PMTs | 2 | 52
Controller for shutter | 1 | 53

Table 6: Components of the controlling module
Control box shell | 1 | 27
Control box cap | 1 | 28
MEMS driver (controller) BDQ PicoAmp 5.4 T180 | 1 | 44
Connectors J1,J2 | 2 | 44
BNC male to BNC male | 8 | 95
DSUB15 to 8xBNC cables
DSUB15 connector plug (male) | 2 | 46
back shell | 2 | 47
DSUB15 connector socket (female) | 2 | 48
DSUB15 to 6-pin (pcb/mems) cable
6-pin connector for MEMS | 1 | 49
Single wire cables | 6 | 50

Cleaning and preparing all components.

Step1. All the custom machined components are cleaned with 100% alcohol. Some components are also cleaned in an ultrasonic bath for 10min including the coupling holder (item 23), collimator holder (item 26), and the glass flanges (item 33).
Step2. Spray all the cleaned components in Step 1 with Air duster (item w) and put them aside in a super clean bench.

Assembling the coupling module.

Step3. Put one half-wave plate (HWP, item 41) into the rotation mount (item 4) and screw the mount from the bottom of the coupling box using a M3 cap screw.
Step4. Fix the seed laser source (item 29) and the coupling box (item 21) on the breadboard (item 1) with four sorbothane feet mounted underneath (item 2). Make sure the entrance of the coupling box is centered to the output of the laser source
Note! To test the laser before using it, align its beam path to the Pulse Check autocorrelator (item r) to optimize the settings to remove the profile side lobes and minimize the pulse fit (≈ 100fs) and measure the maximum average power (≈ 1.2W@ 5V).

Step5. Place right-angle prisms (6 prisms, items 34) on the intended positions inside the coupling box (Fig. S7-B in Zong, et al.,2022, and Fig.1 in this document). Attach the surfaces of the prisms to the inner wall of the coupling box as close as possible. Then add drops of super glue in the contact points. Hold the prisms for a few seconds until they are fixed.
Note! Switch on the laser, place NIR Detection Card after the glued prisms to confirm the prisms were glued correctly, leading to an aligned laser beam path as designed.

Step6. Glue three glass rods (items 32) on the designed positions inside the coupling box (Fig. S7-B in Zong, et al.,2022, and Fig. 1 in this document) Check the laser spot after the glass rods. If centered, drop super glue on contact points of the box’s base and the glass rod and press the latter.
Step7. Make two prism assemblies by gluing a prism (item 34) on top of a thick circular silver mirror (item 42). The thick circular silver mirror acts as an adapter to hold the prism on the mirror mount (see Fig. 2).


Figure 1: Placement of coupling box in front of the seed laser, illustrating the components assembled inside as described in this protocol. The right-angle prims are labeled from P1 to P8, glass rods from R1 to R3 glass, Half-wave plate as HWP, mirror mounts as MM1 and MM2 and, finally, coupling holder as CH.

Figure 2: Mirror mount fixated within the coupling box (top) with a schematic of the gluing of the prism on top of a silver mirror (bottom left) with prism centered on the mirror (bottom right).

Step8. Fix the two mirror mounts (item 4) to the coupling box’s base by tightening two M4-screws. The two Hex Adjusters of each mirror mount should face to the two diagonal holes on the vertical walls of the coupling box, such that adjustment of the mirrors’ tilt/pitch can be done from outside of the box.

Step9. Mount the two prism assemblies made in Step 7 on the mirror mounts. Switch on the laser, place a NIR Detector Card before and after P7 and P8 (see Fig.1) to check the alignment of the light path. The laser should pass through the exit hole of the coupling box. If not, adjust mirror mounts until you see the laser from the output hole.
Step10. | Mount the coupling lens (item 40) to the coupling holder (item 23) (see Fig. S7-
B in Zong, et al.,2022) and fix the coupling holder onto the coupling box by screwing it from the outside.

Preparing the HC-920 fiber assembly

The HC-920 assembly building video tutorial can be found on the link: https://www.youtube.com/watch?v=HjAtoPbDu8E

Step11. | Cut about 2.5-meter HC-920 (item 31).
Caution! Throughout this and next steps, keep the fiber straight, always without nods, to not break or damage it.
Caution! Extra length at both ends of the fiber are added because multiple cuts are usually needed before obtaining a very flat and clean tip.
Step12. | Prepare ~ 1-meter heat shrinkage tube1 (item 7). Slide the HC-920 fiber
prepared in step11 inside the tube1. Attach tube1 with medical tape ≈10cm away from one of the ends to hold it in place for a temporary fixation.
Caution! Leave enough space (approx. 10 cm) between the top edges and the tube1 to avoid cutting the jacket if a flat tip was not obtained.
Step13. | Slide the prepared HC-920 into the Coupling protector (item 24). Add two
pieces of short heat shrinkage tubes with length of 10 cm for tube1 and 2 cm for tube2 (items 7) - see Fig. 3.
Caution! Must put the coupler protector before put shrinking tubes on.


Figure 3: Preparation of HC-920 fiber assembly: before cutting the fiber tips (steps 15-16), slide (A) the coupling protection;
(B) heat shrinkage tubes through the HC-920 fiber.
Step14. | Prepare the other end to the collimator with three pieces of shrinking tube: 5cm
of tube1, 2cm of tube2 and 1.5cm of tube3 (see items 7). Slide them over the HC-920.
Step15. | Remove about 2cm protecting claddings of the HC-920 on both ends by using
a fiber stripping tool (item b). Clean with a paper tissue dipped in 100% ethanol.
Step16. | Cut both ends of the fiber with the fiber cleaver (item c) based on the operating
manual provided by Thorlabs. (https://www.thorlabs.com/drawings/50b56cf6fa45ca70-9FCDC893-D86A-5263-EDF4AC19BAB469A9/XL411-Manual.pdf)
Note! About 5 mm uncladded fiber should be kept on both ends (Fig. S8A-C). Check the ending tip quality under the stereoscope (see Fig. 4). If the ending tip is not flat and clean, re-do steps 15-16.
Note! You may also need to shorten the jacket to exposure enough length of fiber on the ends.
Step17. | Slide a cleaned glass flange (item 33) on one of the prepared ends of the HC-
920 with a curved tweezer (see Fig.5-A). Stop sliding the glass flange as soon as the end of the fiber tip is slightly sticking out at the other end of the flange (see Fig.4-A).
Caution! Do not touch the tip of the fiber, as this may damage it.
Step18. | Add UV-glue using a small fiber tip (see Fig.5-B) to the funnel at the root of
the Glass Flange. Wait for the glue to flow up. Repeat until the gap between the HC-920 and the glass flange is filled with glue, then curing the UV glue with UV light.
Step19. | Prepare the other end of the fiber as in steps 17-18.


Figure 4: Schematic of HC-920 fiber inserted into glass flange with tip sticking out on the top side of the Glass Flange (left). Illustration of (A) a good fiber tip; (B) a bad (not flat) ending tip.

Figure 5: Assembling of a glass flange to one of the ends of the HC-920 fiber: (A) Insertion of a cleaned glass flange around the prepared end of the fiber using a curved tip tweezer; (B) gluing of the flange to the fiber by adding glue to the funnel at the root of the glass flange using a small fiber tip; (C) curing process with UV light.

Preparing the fiber collimator

The video tutorial can be found on the link: https://www.youtube.com/watch?v=HjAtoPbDu8E

Step20. | Fix the collimating lens (item 43) into the collimator holder (item 26) by using
optical adhesive (item l) (see Fig. 6)
Caution! Pay attention not to drop glue on top of the collimating lens. Also, do not use too much glue because it can flow down to the hold for the glass flange. To prevent this, flip the collimator holder and cure the adhesive on the other side as well (item e).


Figure 6: Schematic showing the four different components making up the assembling of collimator to the HC-920 fiber. A distance between the HC-920 fiber tip and collimator lens is optimized to attain collimated light when the laser beam that originates from the HC-920 fiber passes through the lens.

Step21. | Temporarily fix the collimator holder on the fiber coupling stage with
collimator assemble tool (items 10 and 25) as shown in Fig. S8E-F in Zong, et al.,2022 & Fig.7 in this document. At the same time, fix the glass flange in the clamp (item 11). Align the center of the glass flange with the center of the collimator holder, and slowly slide the glass flange into the collimator holder, by using the 3-axial adjustment on the stage (item
8) (Fig.S8E in Zong, et al.,2022).


Figure 7: Collimator holder fixated on the fiber coupling stage (left) with end of HC-920 fiber inserted in the clamp and glass flange inserted in the collimator holder. This also illustrates a section of the wider jacket (bottom right side).

Couple the laser light into HC-920 fiber (the video tutorial will be provided soon…).

Step22. | Place another fiber coupling stage in front of the coupling holder (item 11)
which is attached to the coupling box (Fig.S8D in Zong, et al.,2022 & Fig.8 in this document).

Figure 8: Fixation of glass flange into the clamp and insertion of the flange into the collimator holder.

Step23. | Monitor the laser power by using a power meter (item g) from the output of the
collimator. Adjust the mirror mounts in the coupling box and the distance between the glass flange and the coupling lens until the output power reaches about 70% of the input power (measured in front of the coupling lens) – see more details of this on Steps 24-25 of Laser alignment.


Figure 9: Illustration of both ends of HC-920 fiber placed on stages: first end in front of the coupling holder (top left side of both figures) and the other end aligned to the collimator holder. This figure also demonstrates the monitoring of the laser power using a power meter in front of the collimating setup. In this step, by adjustment of the distance between the glass flange and the coupling lens (Step22-1, left figure) and of the mirror mounts (Step 22-2, right figure), an ≈6% increase of power is demonstrated

Laser alignment

The video tutorial can be found on the link: https://www.youtube.com/watch?v=HjAtoPbDu8E)

Step24. | Mount SM05 threaded adapter (item 13) into stage mount (item 10). Connect
patch cable of the handheld red laser source (item f) to threaded adapter.
Step25. | Adjust the two mirror mounts (MM1, MM2 of Fig.1) of the coupling box back
and forth until both red laser (item 13) and green laser output overlap all the way to the coupling box entrance hole. Remove then handheld laser source and replace it by the photodiode power sensor (item g).
Step26. | Adjust the stage that supports the HC-920 glass flange. Slide the flange inside
the coupling holder and stop when the maximum power is reached (see Fig.9-1).
Step27. | Adjust the two mirror mounts (MM1, MM2 of Fig.1) of the coupling box back
and forth, i.e., start with one of the mirror mounts and adjust the top screw while the power increases, and stop when it decreases (see Fig.9-2). Continue with the other mirror mount, also adjust the top screw, and repeat this process to maximize the power.

Step28. | Repeat Step 27, but for the latter adjust bottom screws of both mirror mounts.
Step29. | Adjust the HWP to further maximize the output power after the HC-920 fiber.
Step30. | Glue the glass flange to the coupling holder by initially adding small amounts
of optical adhesive (item l) to cover the gap between the two. Cure it with UV light (item
c) for 60s to fixate it. Fill the gap with more adhesive and cure it again for 100s.
Step31. | Open the clamp and move the stage z-axis down, away from the fiber. Slide heat
shrinkage tube 2 (item 7) up, until it covers the glass flange, and use heat gun (item q) to shrink it. Add epoxy (item p) to the contact points.
Caution! When moving the stage down, first do this with the small cursor while monitoring the power, to make sure it is stable. When the stage is far enough from the HC-920 fiber coupling end, move it away.
Step32. | Slide the coupling protector (item 24) over and fixate it to the coupling box with
M2 screws (item t). Then slide heat shrinkage tube2 such that it enters the coupling protector and use epoxy to fixate it well to the coupling protector (see Fig. 11-1).
Step33. | Move the stage under the glass flange (collimator side) away or closer, until the
output beam is collimated (see Fig.S8-G).
Note! Check the shape of the spot at the exit of the collimator (Fig.10-A) by following the green laser beam with a NIR detector card and fixate the latter ≈2m away from the collimator. A very sharp hexagonal-star-shape spot with a gaussian-profile-like intensity distribution in the center, as show in Fig. 10-B, should be visible.

Figure 10: Laser output shining on a NIR detection card placed in front of the collimator (A) and 2m away on a nearby wall (B), confirming the light is collimated after passing through the coupled HC-920 fiber and collimator.

Step34. | Fixate the glass flange to the collimator holder adding small amounts of optical
adhesive (item l) and cure it for 60s.
Caution! Ensure that the laser spot described in Step31 does not change during gluing.
Step35. | Repeat Step34, adding more adhesive. Cure it for 100s.
Step36. | Slide the three thickness heat shrinkage tubes (item 7) of different thicknesses
towards the collimator holder and add epoxy to hold them: 1st tube1 to cover the fiber without the jacket; 2nd tube2 to cover the glass flange; (3rd) tube3 to cover the gap of HC-920 end and the collimator holder base (see Fig.11-2).
Note! For more details, check video tutorial HC-920 assembly, especially regarding the technique to heat shrink the three thickness tubes.
Step37. | After the epoxy is dry (overnight), remove the collimator stage.


Figure 11: Illustration of the fiber’s ends protected with jackets and connected to (1) coupling box, covered also with coupling protection; (2) collimator holder and epoxy is placed on top to join the jackets.

Assembly of the detection module.


Taken from Fig.S7-C in Zong et al., 2022

Prepare the Cage Cube for Fluorescence Filter Sets
Step38. | Separate the removeable insert (item 14) from its base (item 15) (see Fig.S7-C
in Zong et al., 2022)
Step39. | Open the Cube Top removed on Step38 by untightening the two retaining
screws (3/32” hex) and remove half-part of the cage
Step40. | Untighten the top two screws with a Phillips #00 screwdriver to loosen the leaf
spring and slide the dichroic mirror (item 38) under the clamps (see arrows in Fig.12-A). Place the coated side of the mirror facing the direction from where the laser beam comes from. Tighten the screws enough to hold without breaking the mirror (see Fig.12-B). Caution! Do not touch the mirror, so best is to place it on the slit holding a tweezer from the corner.
Caution! To confirm which side is coated, place a tweezer with the tip very close to the mirror surface and choose the side which does not have a ghost reflection on top of the real reflection. Caution! Only light force should be applied to tighten the mirror to prevent it from moving.
Step41. | Mount back the other half of the cage and prepare the filters to assemble on the
next steps (see Fig.12-C)

Figure 12: Kinematic cage mounting steps for assembling the dichroic mirror inside the removeable cube top (A-B) and filters on the side ports (C)

Step42. | Place the cage rotated 90 degrees from its standing position with the frontside
filter port facing up.
Step43. | Remove the threaded retaining ring using either a tweezer or Spanner Wrench
2 (item d) by rotate it anti-clockwise.
Step44. | Insert the shortpass filter (item 37) with the coated side facing up and outwards,
i.e., direction of beam light.
Caution! Follow tips of Step40 to identify the coated side.
Step45. | Place the threaded retaining ring on top of the filter and with the Spanner
Wrench 2 slightly tilted, rotate it clockwise until the ring is all the way down, in contact with the filter.
Caution! Make sure there is no gap between the ring and the filter. And that the filter does not wiggle if shacked, meaning it is secure.
Step46. | Mount the 525nm and 630nm emission filters (item 35,36) on the ports as
labeled in Fig.13. For each filter, follow Steps 40-42.

Figure 13: Top view of a possible Kinematic cage configuration. The labels indicate the assignment of the filters relative to the incoming beam from the TFB. LP750 stands for 750nm lowpass filter; 525-39 and 630-69 correspond to the emission filters with centered wavelength on 525nm and 630nm with FWHM of 39nm and 69nm, respectively.

Step47. | Close the empty filter port (right side of Fig.13) with an End Cap for machining
(item 17)

Mounting TFB to kinematic cage

Step48. | Prepare a SM1 Coupler for external Threads (item 18) and place the two rotating
halfway. Attach it to the shortpass filter port.
Step49. | Thread the shutter mounting adapter (item20) to the Coupler of Step48.
Step50. | Mount the optical beam shutter (item 19) after Step49 by screwing it clockwise.
Step51. | Mount an aspherical lens (item 36) on a two connected lens tubes (item 16) and
place a threaded retaining ring on top to prevent it from moving and crash with the shutter of Step49.
Caution! The flat surface of the lens must face the TFB (outwards of cage) to collimate the beam in the direction of the kinematic cage (convergent point from the light guider to parallel laser beam rays entering the filters cage) – See Fig. 14.
Step52. | Confirm that the light coming out of Lens tube of Step51 is collimated. For this,
attach a green LED (item h) to the mount and follow visualize spot changes by approaching and distancing the assemble relative to a white wall (see Fig.15)


Figure 14: Top (A) and bottom view (B) of two Tube Lens attached together and an aspherical lens mounted inside showing its curved and flat surfaces, respectively. (A) is the side facing the shutter and (B) facing the TFB.

Figure 15: Checking output light from TFB after passing through aspherical lenses and before entering the kinematic filter cage.

Step53. | Assemble the mounted lens on Step51 after the shutter (see Fig.16-A).
Step54. | Thread the sprayed TFB (item 30) at last.
Caution! Before adding the TFB, coat it with black rubber spray (item x) because of its grey coating. One way to ensure its uniformity is by holding it vertically and spraying very fast around 8-10x times. Wait until it dries and repeat once or twice.
Step55. | Fixate the assembled kinematic cage on top of the coupling box as shown in
Fig.16(A-B).


Figure 16: Side (A) and top view (B) of the kinematic cage connected to TFB via LP750 filter port. The cage is placed on top of the coupling´s box cap and the Tube Lenses with aspherical lenses inside are also mounted on the emission filters ports, to be connected to the PMTs (see P5.3).

Connecting PMTs to kinematic cage

Step56. | Mount another aspherical lens on Lens Tube (item 36) with flat surface facing
the PMT (outwards of kinematic cage port). Add a threaded ring to hold it in place.
Step57. | Assemble the prepared lens tube on Step56 to the Kinematic cage threading it
on the 525-emission filter port (left side – see Fig.16-B).
Step58. | Thread SM1 Coupler (item 18) to the Lens Tube with external side facing out.
Step59. | Turn off any room light. Connect PMT1 (item 52) (green channel) after coupler
of Step58. Rotate it clockwise until it is fixated. Adjust the position of the middle coupler such the PMT is in a vertical position.
Caution! When opening the PMT lid, there must not be any light source in the room to avoid damage of the PMT anode and shorten its lifetime.
Step60. | Repeat steps 56 to 59 for the 630nm emission filter port and respective PMT2
(item 52) (red channel). The result is show in Fig.17

Figure 17: Kinematic cage connect to PMT shutter, TFB and PMTs assembled on top of the coupling box´s cap.

Mount the μTlens driver and controller for Shutter

Step61. | Fixate the Table mounting plate of the μTLens Driver (item 51) onto the core
optics breadboard (item 1), next to the Coupling box (item 21). Fixate it with two M6 cap screws (item 6), each with a washer as shown on the left side of Fig.18.


Figure 18: Placement of μTLens base on the breadboard and how its Driver is fixated to it.

Step62. | Mount the μTLens Driver unit on top of the magnetic plate and hold it in place
by clipping both ends inwards.
Step63. | Place the shutter controller after the μTLens Driver as shown in Fig.S7-A in
Zong et al., 2022.

Assembly of the controlling module

There are 8 input signals (BNC cables, see Fig.S9-A) connecting to the controlling box (black box in Fig.19) which then give a signal to the MEMS controller (item 44) and has as output six wires that are connected to the miniscope.


Figure 19: Illustration of the coupling box with both Input Cable from the vDAQ (left) and Output cable to the miniscope (right). An arrow on the box side indicates the direction of the signal.

Step64. | Place the MEMS controller (item 44) inside the control box shell (item 28) and
split the grey connector on the input side (connector J1) by splitting each wire.
Step65. | Attach each input DSUB15 (item 46) to the J1 connector (see Fig.S7-D in Zong
et al., 2022) to, i.e. three grounds connected to one another on the input side and to the J1 connector – Pin4 (green lines on Fig.S7-D in Zong et al., 2022).
Step66. | Link also the other pins from Input DSUB15 to J1 connector, as illustrated on
Fig.S7-D in Zong et al., 2022 (black lines).
Step67. | Connect the other side of MEMS controller to 6 pins of J2 connector. The later
then connects to 6 wires bounded with a connector, to be attached to the MEMS. This is the output signal (see Fig.S7-C, right side & Fig.S7-E in Zong et al., 2022)
Step68. | Establish direct connections from input to output, without linking to J1 or J2
connectors. This is illustrated on Fig.S7-C in Zong et al., 2022 (uTLens and LED).
Step69. | Mount the connector socket (item 48) into the backshell (item 47).
Step70. | Attach 8 BNC cables (item 95) for Signal-Input to the DSUB15.
Step71. | Repeat Step70 for output side, but merging the 6 single wire cables (item 50)
that will connect to the miniscope
Step72. | Add a 6-pin connector for MEMS (item 49) at the other end of the gathered
wires of Step67.
Step73. | Close the control box with lid (item 29).
Step74. | Mount controlling module next to the detection module, on top of coupling box
lid as shown in Fig.20 using a M4 capscrew.

Figure 20: Placement of controlling module next to the detection module.

The core optics module has been successfully assembled and the result is summarized on Fig. 21.


Figure 21: Overview of core optics module with coupling box placed in front of laser seed, detection and controlling modules assembled on top of the coupling box cap.

### Part 2- Scope Mounting Assembly

The assembling of the Scope Mounting module is divided in three parts: A) Motorized and rotatable scope holder; B) Head-fixed running Wheel; C) Illumination and Recording. This Protocol includes the main steps to build such module as illustrated in Fig.S7E in Zong et al., 2022.


Taken from Fig.S7E in Zong et al., 2022

Equipment:
- Hex keys (M2.5, M3, M4, … M6)
- Screwdrivers (Cross Slot/Phillips, Hexagon)
- Components of the Scope Holder (Table 1)
- Components of the Head-fixed Running Wheel (Table 2)
- Components of the Illumination and Recording (Table 3)

Table 1: Components of the Scope Holder setup
Component Name | Amount | Item Number (see Protocol S1)
Breadboard | 1 | 54
Sorbothane Feet | 1 | 55
Construction Rail | 1 | 56
Rail carriage | 1 | 57
Precision construction Rail | 1 | 58
Post mounting clamp | 1 | 59
Manual rotation stage | 1 | 60
MINI2P Holder P1 | 1 | 72
DC Motors | 3 | 82
MINI2P Holder P2 | 1 | 73
MINI2P Holder P3 | 1 | 74
Optical Post | 1 | 62
Base for item 58 | 1 | 61
MINI2P Holder P4 | 1 | 75
Hex Screw M2, M2.5 | 1 | 113

Table 2: Components of the Head-fixed Running Wheel
Running wheel (wheel spread + spray) | 1 | 63
Spacer1 | 2 | 64
Spacer2 | 2 | 65
Bearing | 1 | 66
Wheel Holder | 1 | 76
M6 cap screw | 1 | 6
Right-angle clamp | 1 | 67
Pillar posts | 2 | 68
Construction Rail | 1 | 56
Rail Carriage | 1 | 57
Headbar holder | 1 | 77

Table 3: Components of the Illumination and Recording setup
Universal Post Holder | 2 | 69
Zelux CMOS camera | 1 | 79
C-Mount Adapter Lens | 1 | 71
Lens 4.5 or 8.5mm focal length | 1 | 80
Locking Ball and Socket Mount | 9
LED array lights | 1 | 78
LED Power supply | 1 | 78
Basler camera | 1 | 81

Assembling of Motor Stages

Taken from Fig. S7F in Zong et al., 2022

Step1. Fix the construction rail (item 56) to the breadboard (item 54) with four M6x12 mm cap screws (see Fig.22-A) and add the rail carriage on top (see Fig.22-B).


Figure 22: Mount of (A) construction rail to the breadboard; (B) rail carriage and mounting post on top of each previous components.

Step2. Mount all components for the scope holders on the construction rail (See Fig. S7-F in Zong et al., 2022).
Caution! Before assembling the PI motorized stages (item 82), connect the elongated cables to the Motor controller (see Fig. 23), and move the motor to one end of its range by the software to reach the screw holes.

Figure 23: Photography of the DC Motors controller. Only one motor is connected (DC motor 1), yet this controller can allocate up to four motors.

Step3. Fix the precision construction rail (item 57) to its base (item 61). Adjust the height of the scope holder by releasing the M6 screw of the rail carriage on the precision construction rail. Adjust the angle of the scope holder with the rotator (see Fig.24)


Figure 24: Placement of MINI2P Holder P1 (item 72) relative to the manual rotation stage (item 60) and alignment of the latter to the reference line on the right. The top right figure illustrates the assembly of DC motor1(item 82) to the longer side of MINI2P Holder P1.

Figure 25: Illustration of assembling the stage (1-2), MINI2P Holder P3 (3) and MINI2P Holder P4(4).

Assembling of the Running Wheel


Taken from Fig.S7-G in Zong et al., 2022

Step4. Make the wheel spread
i. Cut hardboard (Item 80) to a circular shape (diameter Ø = 17 cm). One of the methods used can be a Jigsaw machine which is dragged in a compass-like movement to make the cut smoother (see Steps i) and ii) in Fig.26).
ii. | Create a hole for M6 screws in the center of the running wheel prepared in i. and for that, use a Drill Tower with a 6mm drill bit placed above the hardboard, as shown in Fig.27.
iii. | Spray the wheel with black rubber spray approximately ten times, until the surface is uniformly opaque black. Between spray sessions, wait ~ 10 min until it dries (see Fig.28).

Figure 26: Hardboard cutting method to make a running wheel. By using a Jigsaw machine with a blade on the end-tip (i), slide it circularly with the desired diameter (in this case Ø = 17 cm) and dragging its blade, pressing the center with the fingers. Repeat one or twice until the circle is well separated from the main hardboard (ii) and then remove it.


Figure27: Illustration of process to create a hole centered on the running wheel hardboard to fit M6 screws. The circular hardboard is placed under the 6mm drill bit of a Drill Tower.

Figure 28: Spraying setup: a hanging wheel between two holes on opposite sides of a paper box.

Step5. Fix the other construction rail (item 56) to the breadboard and mount all components for the head-fixed running wheel on the construction rail, as illustrated on Fig.S7-G in Zong et al., 2022 and Fig.29 to Fig. 32.

Figure 29: Schematic overview showing the disposition of Running Wheel, with construction rail positioned beneath the Motors setup. The Illumination and recording stand on the side.

Figure 30: Schematic of the base to assemble the Running Wheel

Figure 31: Bearing (left) mounted on Wheel Holder (middle) and Top view of the Running Wheel before mounting the wheel itself (right).

Step6. Mount the NIR camera (item 92) and NIR LED (item 91). Adjust the positions of the camera mount and LED mounts (item 87) so the illumination and the camera focus are on the animal`s head.

Figure32: Running Wheel result.

### Part 3- Mobile Cart Assembly

The Mobile Cart Module comprises a breadboard cart which supports a drawer to store microscope objectives and other useful tools (screw drivers, spacers, clean lens tissue, swabs, etc), a rack that has a workstation (desktop computer), acquisition breadboard and controllers for both laser and DC-motors. Furthermore, it supports all the other units (Core Optics and Scope Mounting Assemblies) which are available on top of the larger breadboard. It is the basis of this setup and facilitates the transport and maneuver of the whole system, and so one can compare it to the pillars of a house: without it, the whole structure is not as strong and complete.


Taken from Fig.S7 (H,I) in Zong et al., 2022

Equipment:
- Hex keys for M4, M6 screws
- Philips screw drivers for M4
- Bubble level
- M4, M6 Cap screws
- Components of the Mobile Cart (see Table 1)
- Components for Connecting Cables (see Table 2)

Table 1: Components of the Mobile Cart
Component Name | Amount | Item Number (see Protocol S1)
Mobile Cart | 1 | 83
Main Optical breadboard | 1 | 84
Storage Drawer | 1 | 85
19-inch rack | 1 | 86
Span-In Nuts | 10 | 87
Breadboards for modules | 2 | Items 1, 54
Workstation | 1 | 88
Monitors | 2 | 89

vDAQ – acquisition card | 1 | 90
vDAQ breadboard | 1 | 91
Motion Controller for PI motors | 1 | 92
Controller for 920nm laser | 1 | 93

Table 2: Components for Connecting Cables
Controlling box
BNC cables | 8 | 95
BNC to BNC adapters | 8 | 95

µTlens controller
BNC to SMA male connector | 1 | 96
BNC adapter Female-Female | 1 | 95
SMC connector | 1 | 97
Power supply | 1 | 99

Lasers Controller
Power In Connector
USB B connection cable to workstation | 1 | Included with item 93
Ethernet | 1
D-sub15-connector to Seed Laser | 1
TTL in | 1
Analog In (SMA-connector) | 1
Trigger Out | 1
Keys for Key Switch | 1

Laser Head
AOM connector (SMA cable) | 1 | Included with item 29
Optical Fiber Input | 1
Laser Control Unit Connector | 1

PMT
USB Male A to USB 2.0 | 1 | Included with item 52
SMA to SMB cable | 1 | Included with item 52

Monitor to Workstation
HMI cable | 1
Ethernet cable | 1
USB B (screen) to USB 3.0 | 1

Workstation
USB 3.0 & 2.0 cables | 4
USB-hub (7) ports | 1 | 94
Basler power cable | 1
USB 3.0 Micro-B for Basler camera | 1

Assembling of Mobile Cart

Step1. Lock the casters to assemble the Mobile Cart (item 83) without moving it.
Step2. Mount a 19-inch Rack (item 86) following supplier instructions (see Protocol S1). Step3. Remove the frontal frame from the Mobile Cart and insert the Rack positioned on the bottom frames as shown in Fig.33-A.


Figure 33: Top view of Rack inserted into Mobile Cart (A) and Drawer mounted on top (B).

Step4. Mount the Users tools Drawer (item 85) on the mobile cart following instructions given by Thorlabs (see Protocol S1).
Step5. Add Span-In nuts (item 87) on the front and back rack’s side to later fixate Laser Controller and vDAQ breadboard, respectively (see how these are placed in Fig.S7-I) Step6. On each of the four corners of the Mobile Cart, place an adjustable anti-slip support pad aligned to each of the height adjusters. Using body weight, press the pad down until hearing a click.
Step7. Annex a breadboard (item 84) on top of the four circular adjustable mounts.
Step8. Level the mounts to minimize the breadboard tilt. Use a bubble level to adjust.
Step9. Place the two smaller breadboards (items 1 and 54) on top of breadboard mounted on Step7.
Step10. | Add Scope Mounting and Core Optics assemblies to each breadboard.
Step11. | Attach the Laser Controller (item 93) to the upper section of the front rack.
Fixate it with four M6 screws (see Fig.S7-I).
Step12. | Attach the vDAQ breadboard (item 91) to the back side of the Rack and beneath
the position of Laser Head. Insert M6 screws to the Snap-In Nuts to hold it in place.
Step13. | Place Workstation (item 88) near the bottom rack grids to maximize ventilation.
Step14. | Lay the motion controller for PI motors (item 92) on top of the workstation.

Connecting Cables / Main Connections

For more details of Steps 15-18 & Step 21, please consult vDAQ Datasheet Installation guide (https://vidriotechnologies.com/wp-content/uploads/2022/01/vDAQ-Datasheet.pdf) (see link of Items 90,91 on Protocol S1).

Step15. | Slide workstation cover and remove its second back grid as shown in Fig. 34.
Step16. | Insert acquisition card (see Fig.34-A) through the inside of the CPU with the
connectors sticking out through the open grid´s rack (see Fig.34-B1). Place it between blue and white boards and press it downwards and to the left until it clicks.
Step17. | Before closing the workstation, link the acquisition card to one of the CPU PCI
Express Power Connector (Molex connector) which is a six-pin connector as described in Datasheet Installation Guide. (https://vidriotechnologies.com/wp-content/uploads/2022/01/vDAQ-Datasheet.pdf)
Step18. | Connect the breakout breadboard to the acquisition card. For that, link two
cables from the ports of the former, labelled A and B to the top and bottom ports of the latter (see Fig.34-C and Fig.35).

Figure 34: Assembling of acquisition card (A) in workstation showing front view (B1) and top view (B2) of section where the card is mounted into: on the second grid (B1), placed between the blue and white board. (C) illustrates the power cables connected from A and B channels (left and right) of the acquisition card to the vDAQ breadboard.


Figure 35: Schematic to illustrate connecting A,B - power cables to the vDAQ breadboard backside, top(A) and bottom (B)
(1) from the acquisition card (2, B-left and A-right side, as labelled).
Step19. | Connect three USB 3.0 and a USB 2.0 cables from Scope Mounting Module
monitoring camera (item 79), tracking camera (item 81) and motion controller for PI motors (item 92), respectively, to the workstation ports.

Caution! As there are not enough ports, add extra USB-hub (item 94) on top of the workstation.

Step20. | From the backside of the workstation, connect also to the monitor/screen(s):
HDMI port(s), ethernet cable and USB 3.0 to USB B.
Step21. | Link the connections shown in Fig.S9-A that go from/to vDAQ breadboard
to/from Controlling Module (Signal Input), μTLens Driver, Laser and Shutter Controllers and Tracking Camera.
Step22. | Connect also BNC7 of controlling module to HV Out of μTLens Driver (short
cable SMA to BNC). Moreover, connect the Power of the Driver on the front side. Caution! The μTLens Driver power cable has pins with specific orientation, be careful to place those pins with the correct alignment before pushing them in.
Step23. | Connect a BNC-to-BNC cable from TTL input (front side) of the Shutter
Controller to vDAQ (Digital channel D02). To this unit, link also the Power cable (5V DC, 2.4A) from the backside of the Controller.
Step24. | Finally, attach the Shutter controller to Shutter Head via the jacket next to the
Power, also backside.
Step25. | Link each PMT from its USB Port to the backside of the workstation.
Step26. | Connect the two PMTs SMA output cables (item 52) to the acquisition card
channels 0 and 1. The MINI2P system should be now completed.


Taken from Fig. S9-A in Zong et al., 2022

Figure 36: Diagram showing main connections from vDAQ breadboard to the controlling box (BNCs 1 to 6), μTLens Driver (EXT in), Laser Controller (Analog In and TTL in) and Tracking Camera (via pink BNC connector, to input-2 – see Wiki section of AnimalTracker). (https://github.com/kavli-ntnu/MINI2P_toolbox/wiki/AnimalTracker.vi)

Figure 37: Connections to the back (A) and front (B) of the μTLens Driver, as well as top view (C). HV OUT connects to BNC7 of the controlling module/box (SMC connector to BNC), whereas EXT IN is linked to the vDAQ (SMA to BNC, Analog output AO3).


Figure 38: Top view of Shutter Controller with power on (bottom green LED light) and shutter opened (top green LED light right under enable button). The controller rear view (zoomed-in inlets) shows the main connections: TTL Input to the vDAQ (External Modulation Input), Sutter Head Jacket to the Shutter Head and Power (DC input jacket).

Scan Image configuration*

Controlling module | vDAQ channel | ScanImage
1_X | AO1 | Dabs.generic.GalvoPureAnalog (slow axis) Control channel/…/AO1
2_Y | AO0 | Dabs.mirrorcle.ResonantAxis (fast axis) Zoom control channel/vDAQ0/AO0 Filter clock DO channels X – D3.1 fast filter Y – D3.2 slow filter
3 +5V | +5V
4 EN | D0.1
5 Fx | D3.2
6 Fy | D3.1
7 TLens | HV out piezo controller
8 | - | LED not in use

*Settings vary depending on the MEMS scanner, if MEMS-L or MEMS-F.

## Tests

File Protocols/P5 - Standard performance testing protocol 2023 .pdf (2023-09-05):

## P5 - Performance Tests & Standard Testing Protocol

This protocol includes preliminary testing of a MINI2P system (Steps 1.1-1.5), laser calibration after the scope´s objective (Step 2) and four other steps for miniscope calibration (Steps 3-6). An overview of these steps is shown below.

## Overview of key steps

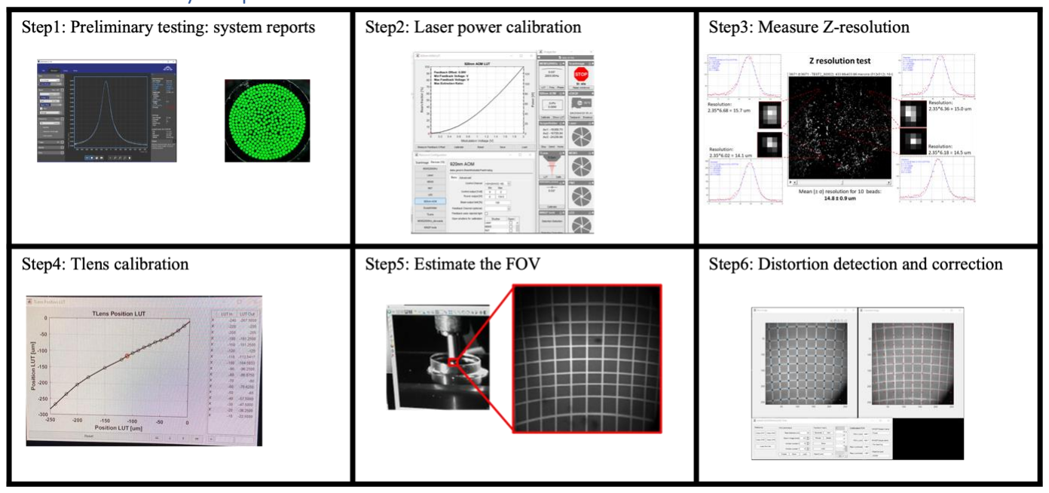
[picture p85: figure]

### Reagents and other equipment

Component Name | Supplier | Part Number/ #Item
Assembled MINI2P 2022/2023 + Objective D0309* | LabMaker/self assembled | Several + #113*
Power meter and photodiode | Thorlabs | #g
Universal post holder | Thorlabs | UPHX/M** (#69)
Optical posts (x4) | Thorlabs | TRX/M** (#62)
Distortion grid | Thorlabs | #n
Fluorescent marker/highlighter | - | #n
Headbar for MEC (or CA1, V1) | 3A prototype | #120
Glass plugs (x2) | Sunlight | (new!) #121
Cover slips | Sunlight | (new!) #122
FluoSpheres beads | ThermoFisher | (new!) #123
Distilled water or ethanol | - | -
Distortion grid setup
Rail carriage | Thorlabs | XT95RC4/M (#57)
Kinematic rotation mount | Thorlabs | (new!) KS1RS (#124)
Beads setup «scope mounting»
Rail carriage | Thorlabs | XT95RC4/M (#57)
Quick-connect goniometers (x2) | Thorlabs | (new!) XRNG2/M (#125)
Headbar holder | 3A prototype | #57
M4 screws (x2) | - | -
M3 screws (x2) | - | -

*The miniscope calibration example can be adapted to air objectives too by just removing the cover glass placed on top of the distortion grid and bead sample. ** Variations of these items with different heights are suitable too (X=75, 100, …)

### Step1. Preliminary testing: system report

Before starting the miniscope performance tests, ensure the system report requirements and designed parameters have been fulfilled according to Table 1. Each design parameter comes with examples of test-results and referenced to other protocols.

Table 1: System report designed parameters with acceptable values.
Step | Design parameters | Acceptable values/ Minimum Requirements
Test results
(examples)
1.1 HC-920 Coupling efficiency | & output shape | >70% after collimator Sharp, Gaussian-profile distribution in the center | Fig.1.1
1.2 | Pulse width & shape | <130 fs (after the HC-920), Lorentz fitting, minimized side lobes, stable | Fig.1.2
1.3 GFB efficency | & dead cores | > 70 % of green laser input (535nm) < 4 dead cores | Fig.1.3
1.4 | System wiring | Breakoutboard to controlling box and other components Confirm MDF channels | Fig.1.4
1.5 | Connect MINI2P | Insert HC-920-PM collimator Attach GFB/TFB Align collimator to MEMS mirror center | Fig.1.5

1.1 HC-920 coupling efficiency: defined as the ratio of the output power measured after the collimator, and the power at the exit of the coupling box before the coupling lens. It must be equal or higher than 70% (it typically does not exceed 80%).

Laser beam output: shape of the spot at the exit of the collimator holder must be sharp (not blurry) and with a Gaussian-like profile distribution in the center. The shape differs between different HC-920 fiber versions, as follows:
- K50-060-70: hexagonal-star shape or 4-pointed rounded symmetric star (Fig.1.1-a)
- K60-060-PM*: stretched oval shape (Fig.1.1-b)
* HC-920-PM is the only fiber commercially available by NKT Photonics as of July 2023
a) b)

Fig.1.1: Collimated laser output shape after passing through 2.2-2.3-m long HC-920 fiber and collimator on a NIR detection card placed 2-3m away for two HC-920 fiber versions: (a) K50-060-70 and (b) K60-060-PM.

1.2 Pulse width is also measured after the collimator. A set of mirrors are placed in front of the collimator with an angle to reflect the output laser beam to the autocorrelator entrance slit. With correct alignment, a light should be visible at the autocorrelator grid and centered in the cross. Run APE Pulse Check as shown in video tutorial “HC-920 assembly” to measure the Pulse width by curve fitting a Lorentzian. Change the laser GDD (via Toptica/Sparklaser software) and rotate the half-wave plate (HWP) inside the coupling box such the side lobes and pulse width (<130 fs) are minimized.

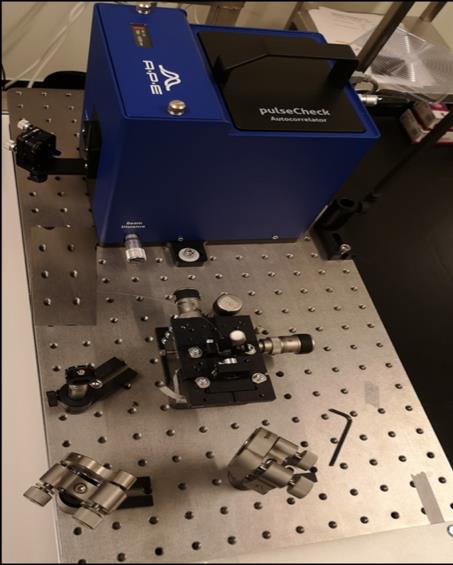
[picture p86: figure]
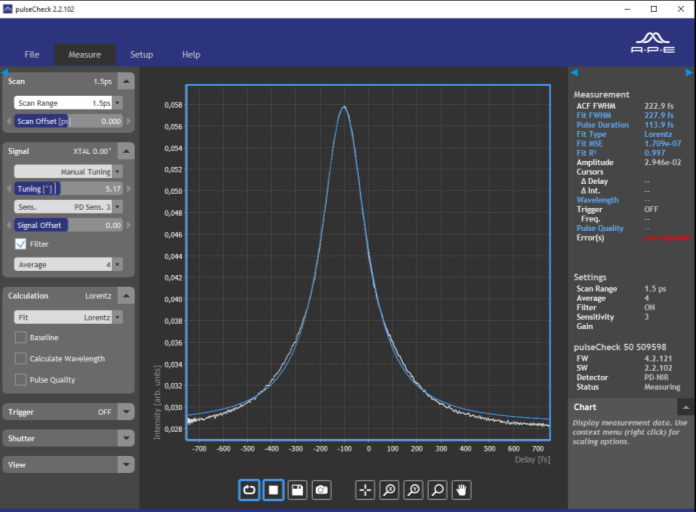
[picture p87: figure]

a) b)

Fig.1.2: (a) Setup to measure pulse width; (b) Pulse plot measured by APE autocorrelator, with Lorentzian fitting and GDD for 2.2m HC-920-PM fiber.

1.3 GFB efficiency: connect a green LED through one of the ends with the SMA connector (see Fig1.a) with fixed input power (around 30mW) and then measure the output power at the other end using a photodiode sensor connected to a power meter (select green laser wavelength ~ 530nm). GFB efficiency of 70% or higher is ideally recommended.
Efficiency lower than 60% does not meet the standard requirements for the MINI2P platforms. The second test is to visualize the fiber cores under the microscope while shining green light with a green laser through the SMA end. An ideal GFB should not have more than 3-4 dead cores (see Fig.1.3-b). Both steps were described in GFB assembly tutorial protocol.
a) b)

Fig.1.3: TFB/GFB standardized performance tests: (a) measuring efficiency with a 530 nm green laser; (b) fiber illuminated cores under a microscope (with 1 dead core).

1.4 System wiring
This step is especially important to ensure all BNC cables are correctly connected from the breakout board channels to the controlling box, TLens driver, PMT shutter and laser, as illustrated in the schematics of Fig.1.4 and Table 2. The next steps are recommended as follows:
i. Load the Machine-data-file (MDF) suitable for the MEMS mirror (2000Hz for Slow or Large-FOV and 5600 Hz for Fast-FOV) when starting ScanImage. Load also Configuration settings given.
ii. | Double check all connections, especially between breakout board (AO/D) channels and
| control box, but also to PMT shutter, laser controller and TLens driver.
iii. | Open the different MDF tabs on File>Machine configuration to confirm the breakout board
| BNC connections match the selected AOX/DX in the ScanImage main tabs.
CAUTION! MEMS x-y axes and correspondent filters channels were swapped on ScanImage MDF to guarantee a more square-FOV. This can be reversed, just make sure to match the fast axis with its fast filter, and slow axis to its slow filter.

For a more comprehensive matching, please check MDFs available on GitHub (https://github.com/kavli-ntnu/MINI2P_toolbox/tree/main/Software/SI%20settings) for 2000Hz (slow MEMS, L-FOV) and for 5600Hz (fast MEMS, F-FOV).

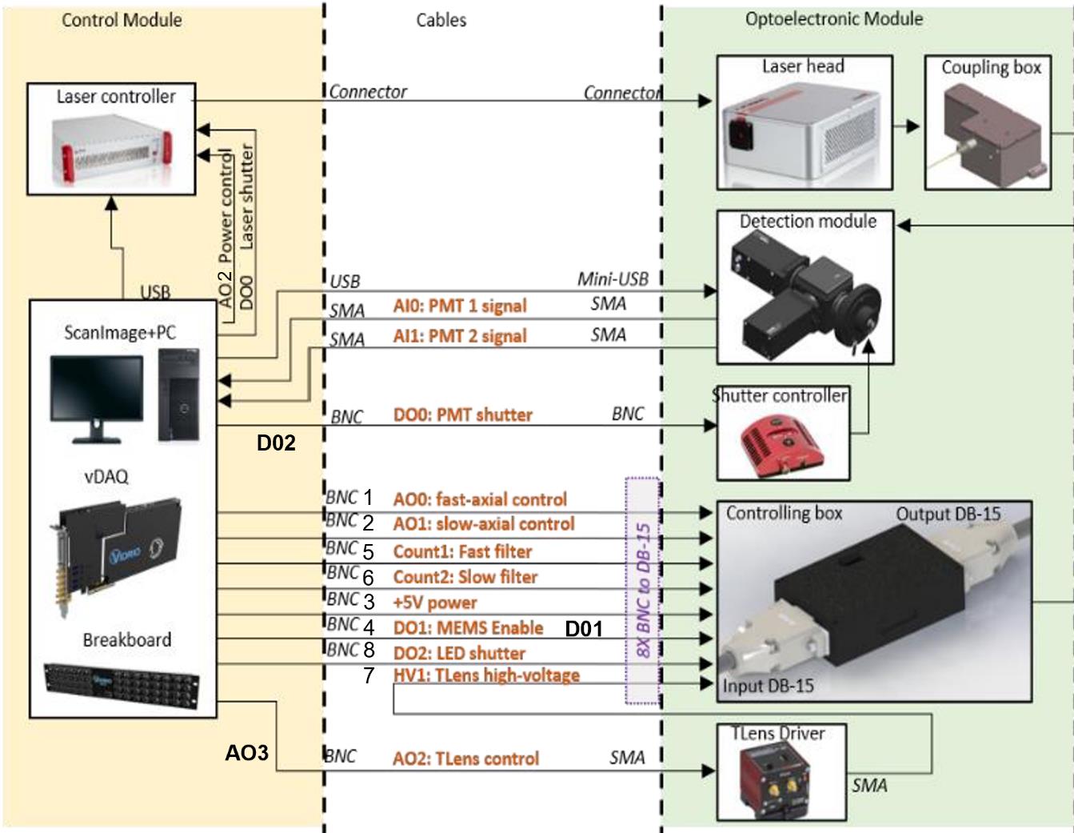
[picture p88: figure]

Fig.1.4.: System wiring with focus on connections from the vDAQ breakout board to the control box, laser, TLens and PMTs.

Controlling box input, BNC connections (1 to 8) is illustrated in Fig.1.4. All BNCs are directly connected to breakout board channels (see Table 2), except BNC7 which is connected to TLens driver. Digital shutters are also shown for laser (D0.0), PMT (D0.2) and MEMS enable (D0.1).

Analogue output channels, AOX are displayed for TLens driver (AO3), laser controller (AO2) and MEMS fast and slow axes (AO0-AO1).

Table2: Correspondence between breakout board channels connected to controlbox (BNC 1 to 6) and driver (BNC 7) to MDF tabs in ScanImage for fast MEMS (5600Hz).*Axes were swapped for a more square FOV, yet filter clocks must match the swap otherwise MEMS can break.

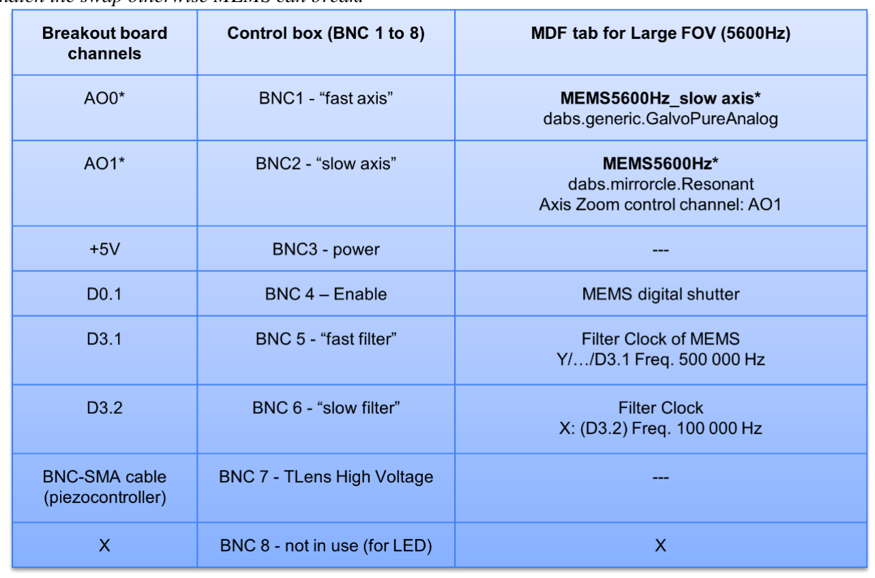
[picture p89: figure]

1.5 Connect MINI2P to system

i. Insert collimator holder all the way into scopebody P1 slit.
ii. | Fixate HC-920 fiber collimator in an optimal position: beam hits the center of the MEMS
| mirror, and the reflected beam output should look oval and symmetric as in Fig.1.5-b.
| Caution! No MEMS circuits should be visible on the sides in the reflected beam output
(Fig.1.5-b).
| Tips! If collimator is loose, screw a M1.2 to fixate it.
iii. | Insert GFB/TFB into scopebody P3 slit until there is some resistance.
| Caution! Do not push too hard in as it can break the dichroic mirror.
| Tips! Instead of a screw to fixate it, it is possible to add some tack-it around it.
iv. | Connect the MEMS flex cable (PCB) to the 6-wires connector (black end facing clip)
| Caution! Before attaching the MEMS flex cable to the MEMS 6-wires connector please
remember to disconnect the controlling module power (5V) and to disable the piezocontroller HV.

a) MINI2P connected to system | b) laser output after objective with ScanImage in PARK

Fig.1.5: MINI2P mounted to system (a) and beam output after miniscope’s objective after being reflected on the MEMS mirror (b) centered on the MEMS mirror. If non-centered, the MEMS circuits are visible on the edges of the beam output. ScanImage is on PARK and laser power is ~ 30%.

## Step2. Power laser calibration

2.1 Calibrate laser look-up-table (LUT) by measuring power output with a photodiode (item #g) placed in front of the objective (see Step 18 of Prototocol P4, part 2).
2.2 Update normalized values to 920 AOM.beamlut (https://github.com/kavli-ntnu/MINI2P_toolbox/blob/main/Software/SI%20settings/920nm%20AOM.beamlut) located in the same folder as the MDF (e.g. C:\SI settings\2022\...).
Tips! Measuring in steps of 0.2V from 0 to 2V is typically enough range for Ca²⁺imaging.
Note! Normalized output power (Fig.2) is the ratio of measured output power after the objective by the maximum power at 2V, i.e., in the illustrated case all power values were divided by 134.5mW.

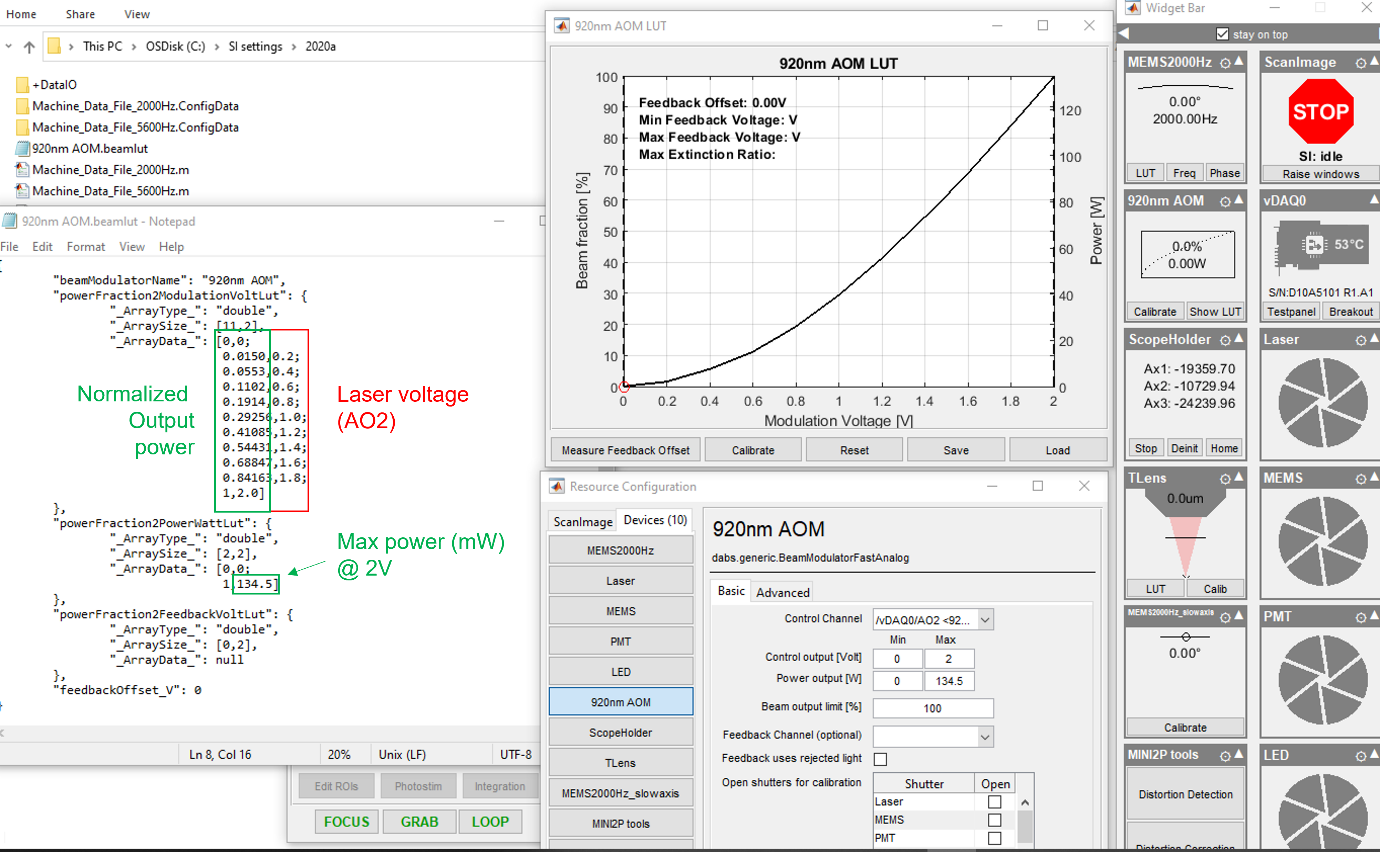
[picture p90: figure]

Fig.2: 920nm AOM beamLUT file of laser calibrated from 0-2V in steps of 0.2V with maximum power of 135mW (left); ScanImage laser LUT of beam fraction (in %, left vertical axis) and power (in mW, right vertical axis) as function of laser AO voltage (top bottom); MDF AOM tab delimitating voltage and power.

920nm AOM.beamlut file is available on GitHub under MINI2P_toolbox/Software/SI settings/ (https://github.com/kavli-ntnu/MINI2P_toolbox/tree/main/Software/SI%20settings)

## Miniscope calibration (steps 3-6)

Table2: Designed parameters with acceptable requirements for a high standard miniscope.

### Step Design parameters Acceptable values/ Minimum Requirements

### Test results

3. | Z resolution | <16-17 μm with objective D0277 / D0329 | Report results in this column and/or add location of saved data (Z-stack for Res, MDFs with TLens LUT, 3D Transf. Matrix)
4. | Tlens calib LUT | Steps of 10μm along the Z axis Typically, 20-25 datapoints
5. Estimate FOV | | >450 μm x 450 μm, MINI2P-L >350 μm x 350 μm, MINI2P-F At 0 μm plane (after correction)
6. 3D | Transformation Matrix | Distortion detection at every 10μm along the Z axis Total 20-25 matrices
| Speed | 15Hz (MINI2P-L, 256 line) 40Hz (MINI2P-F, 256 line)
| Weight | <2.5 g (without holder and baseplate)
| Z-scanning | Range: >200 µm (up to 240μm)

In this part, the main four standard performance steps (steps 3-6) are provided to calibrate a miniscope (valid for either version, MINI2P 2022 and MINI2P 2023):
Step3. Measure Z resolution
Step4. Calibrate TLens look-up-table (LUT)
Step5. Estimate FOV using MINI2P SI device
Step6. Distortion detection and correction: 3D Transformation Matrix

Before measuring the resolution (Step 3), it is recommended to place a prepared distortion grid (see steps 4-b, 5-6) to check how the FOV looks like with higher zoom. Start with zoom 2.0, and then decrease slowly up to 1.0 (CAUTION! Always stop focus before changing the Zoom, otherwise the MEMS can break). If the FOV looks uniform and the MEMS slow and fast axes settings are adequate, proceed to step 3. Otherwise, open MDF configuration from File Menu, and decrease the applied voltage and/or angle on MEMS tabs until the FOV looks stable and uniform.

For steps 3-4, it is recommended to use a bead sample with 1 μm diameter beads with implant as one would normally do for a surgery yet adapt it for miniscope calibration: the surface of the implant that usually faces the imaging plane is covered with fluorescent beads.

Bead sample preparation
i. Prepare headbar (e.g. for V1): glue a cover glass (Ø4.6mm, 1.5mm thick) to the inner diameter of your headbar, with the top flushed
- Alternatively, use MEC assembly with prism or another suitable implantation. ii. Flip it and spread a small 1μL drop of a diluted bead mix over the cover glass
- FluoSpheres beads (item 123) to distilled water ratio: 1:200 to 1:500, depending on desired concentration.
Caution! Spread the thin drop with a pipette to make a very thin layer
iii. Let it dry for 2h, and only then add a medium gel (index matching the brain) over the beads and fixate a cover slip (item 122) to protect and keep the beads in place.
iv. Place the prepared bead sample holder with M3 screws (See Fig.3)

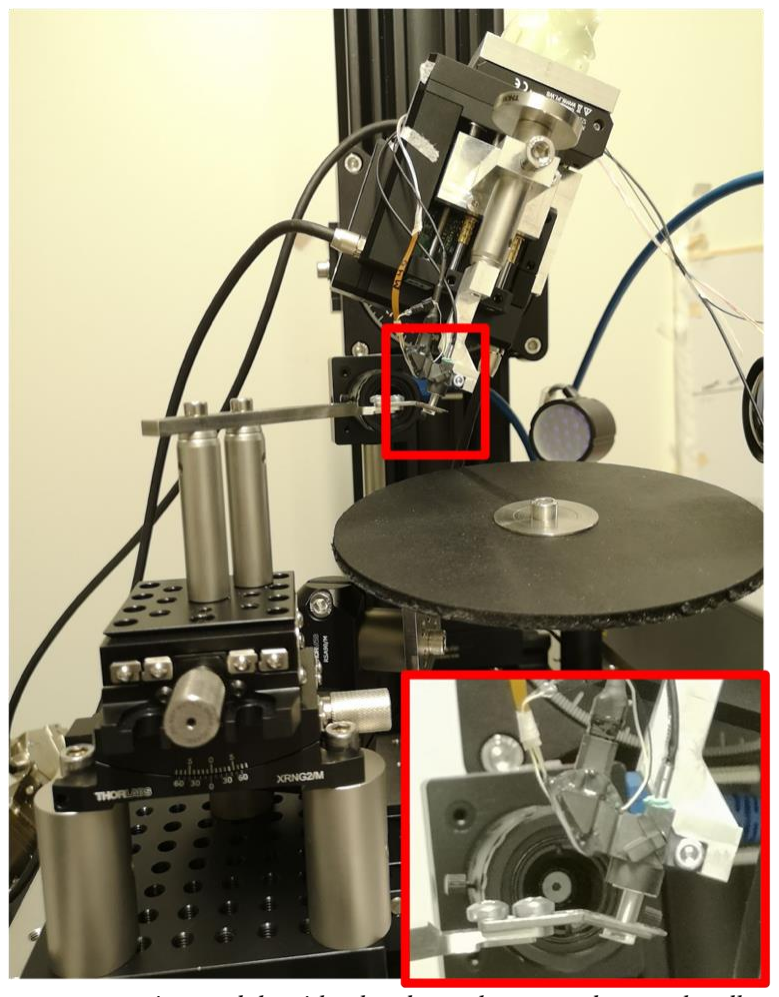
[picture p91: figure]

Fig.3 Example setups for scope mounting module with a bead sample mounted onto a headbar for D0309 objective and zoom-in of scope-to-beads alignment.

## Step3. Measure Z-resolution

For resolution tests and TLens calibration, it is recommended to mimic the implantation configuration in-vivo. Therefore, fix your beads sample into the same headbar type (MEC, CA1 or V1) + prism or glass-plug/cover slit you use during surgery as described before.

To determine the resolution of the miniscope, measure the axial bead intensity distribution by recording a Z-stack of the prepared beads sample around its focus plane. Then select multiple beads across the FOV, and for each individual bead, plot its Gaussian distribution to find the axial resolution, ResZ which can be approximated as:
ResZ = 2√2 ln 2 d ≈ 2.35 d (Eq1)

Where d is the standard deviation of the Gaussian. To determine the lateral resolution, ResXY correct first the imaged z-stacked by applying the transformation matrix determined at the focus plane. Fig.3.1 resumes the image acquisition approach to measure the Z-resolution.

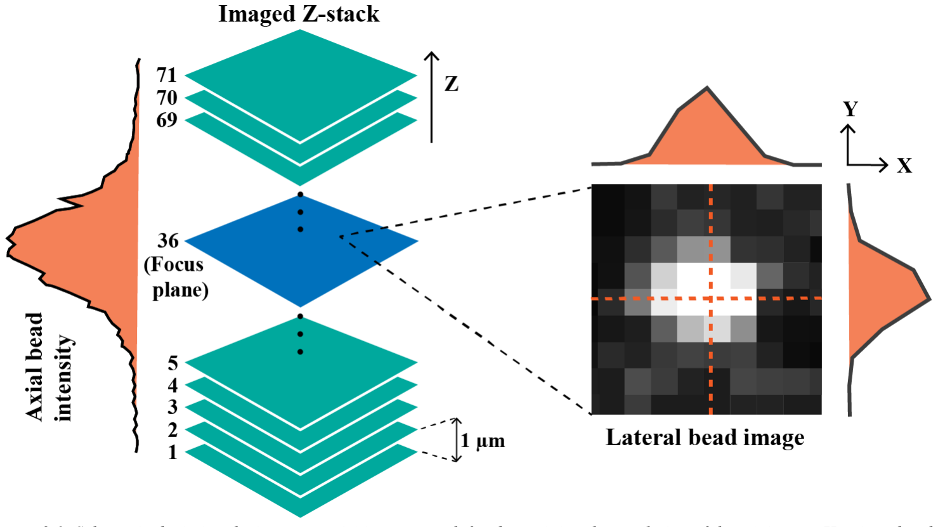
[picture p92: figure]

Fig. 3.1: Schematic depicting the image acquisition approach for determining the resolution of the miniscope. Herein, a bead in the sample will have a three-dimensional PSF, making it possible to plot its intensity along all three axes: X, Y and Z.

Before determining the resolution, first align the beads image to the objective plane as follows: 3.1.Place the prepared bead setup under the miniscope
3.2.Move the stages until you find the focal plane. Optimize the power (typically 15-20mW for a bead solution as the diluted above)
3.3.Align bead sample to scope light output. Manually move x-y tilt goniometers (items #125) placed under headbar holder until there is no clear shift of light.
3.4.Measure a Z-stack of N planes (N-odd number) as described in Fig.3.1.
Tips! To check alignment, a Z-stack with less planes is preferred.
3.5.Open the measured Z-Stack on Fiji and select four outermost regions of interest (RO1 to RO4), as in Fig.3.2. The bead sample is aligned to the scope light output if Z-profile has centered (focus planes) within ±1 pixel.

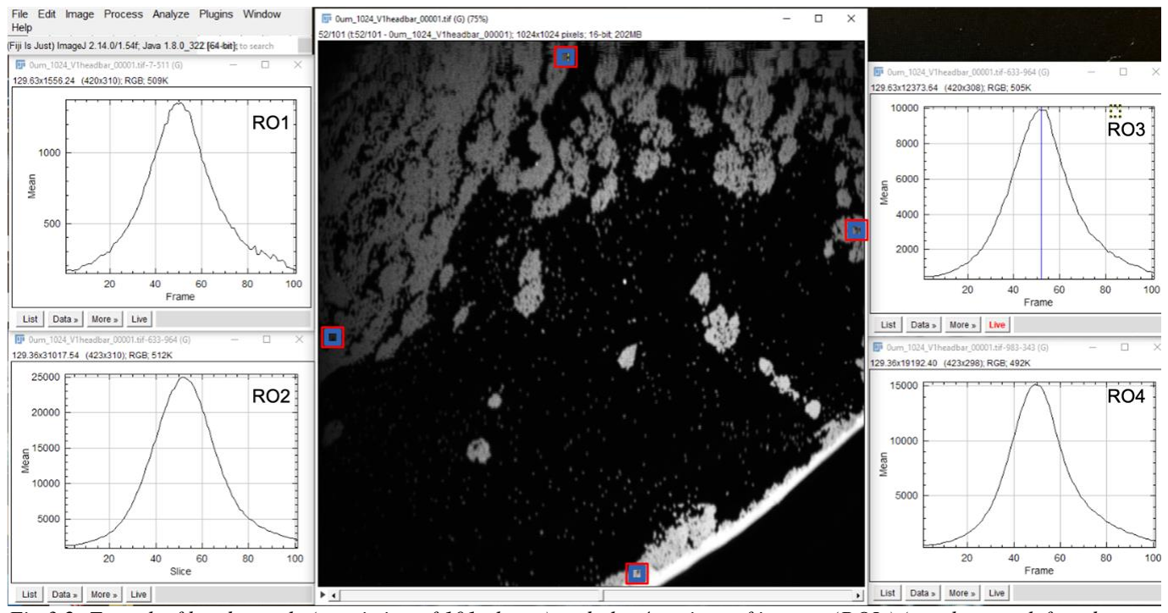
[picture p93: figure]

Fig.3.2: Z-stack of bead sample (consisting of 101 planes) and plot 4 regions of interest (ROIs) (top, bottom, left and right) across the FOV, which have central plane around frame 51± 1 indicating that the headbar beads sample is placed parallel to the miniscope’s imaging plane.

3.6.Around the central plane, image a Z-stack of N planes at 512- or 1024-pixel image size, N being an odd number to guarantee the same number of planes above and below the central focus plane. Note! This step should only be done after the bead sample is aligned as in Step 3.5 and Fig.3.2. Tips! Check if number of planes selected is sufficient such there is complete dark images at the bottom and top planes. An example is given below in Figs. 3.4.
Tips! In examples given a stack of 71 (up to 101) slices, with 10-20 frames per slice was sufficient.

3.7.When ready, click “ENABLE” stack, and average by the number of frames per plane (typically around 10). Click GRAB to record.
3.8.Open the recorded Z-stack with Fiji. Select a single bead with the square cursor, and right click to duplicate stack for this single bead.
3.9.Plot Z-profile of single bead to find brightest plane. Move stack to that plane, adjust contrast in Image>Adjust>Brightness/contrast and press “Reset” at the brightest plane, and click “Apply” all.
3.10. In Image>Stacks plot 3D projection (X or Y, 180 degrees) or orthogonal views to visualize the axial PSF.
3.11. Drag a line along the center of the PSFs as illustrated below.

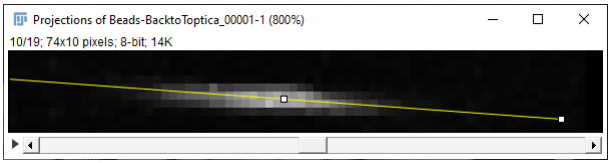
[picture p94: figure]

3D projection of selected bead.

YZ orthogonal view of the same bead.

3.12. Plot the intensity values by clicking Analyze>Plot Profile. Copy the datapoints.
3.13. Fit the profile with a Gaussian curve by clicking Analyze>Tools>Curve fitting, paste the datapoints and select Gaussian. A similar profile as shown at the top-right of Fig.3.3 should be displayed.
3.14. Calculate the z-resolution using Eq (1)
3.15. Repeat steps 3.8-3.12 for at least 10 beads across the FOV.
3.16. To find the miniscope Z-resolution, average its values. A Z-resolution of 14.8±0.9μm is shown in example of Fig.3.4


Fig. 3.3: Single bead zoomed-in of z-stack imaged using motors for 71 planes, 20 frames per plane at 512 pixels. Gaussian bead profile (top right corner) with d=5.72 and Z-Res of 13.4 μm.


Fig. 3.4: Overview of Z resolution tests with example of gaussian profiles of 4 beads. It is recommended to measure Z-Res of 10 beads over the entire FOV and in this example.

## Step4. TLens calibration

a) More precise TLens calibration method focusing on a centered bead
4.1 | Open TLens LUT by pressing TLens “LUT” from the widget bar (see Fig. 4.1)
4.2 | Choose a bead in the center to calibrate the TLens (see Fig. 4.2)
4.3 | Move TLens from the deepest plane, 0um to -20μm which moves the focus up in z-direction.
| Move the linear stage motors down a 20μm step as in see Fig.4.1. This activates the next
| TLens LUT calibration point (in red, Fig. 4.1)
| Tips! If the configuration has the scope 20 degrees rotated, correct x-y stage positions such
| selected bead is around the same position/ROI.
4.4 | Record a stack of N plans, N being an odd number around this focus plane (Centered Stack)
| Tips! In Stack controls, 31 slices, 10 frames per slice, spacing 1μm (using motors) should be
| sufficient. Otherwise, adjust the total number of slices such there are enough statistics for a
| clear Z-profile curve.


Fig.4.1: ScanImage overview of TLens position LUT, with emphasis of calibration showing transition between two datapoints at planes 0 and -20 μm in red, and motors controls tab where <TLens> and motors were moved 20 μm in opposite directions. To the left, example of Z-tack with 51 planes (10 frames per slice) to find Z-profile of single bead during TLens calibration.

4.5 Open the saved Z-stack in Fiji, select a region using a rectangle around the central bead chosen in step 4.1, save the ROI and plot its Z-profile (Image>Stack>Plot Z-axis profile).


Fig.4.2: (top) Z-stack of beam sample (51 slices) for two different Tlens LUT values at -20μm plane (see Fig.4.1, right). (bottom) Z-profiles are displayed for the selected bead around the center of the FOV (red square), showing a shift towards the middle of the stack after correcting the TLens LUT datapoint by moving arrows ↑ or ↑↑.


4.6 If the bead distribution is not centered as shown Fig.4.2-left side, press the arrows pointing downwards ↓ and ↓↓ or upwards ↑ and ↑↑ on the TLens position LUT (see TLens position LUT below) depending on the desired shift direction.

Tips! By pressing on arrows pointing up, the focus plane of Z-profile moves to the left. For finer or cursor tuning, use one or two arrows, ↑ and ↑↑ respectively.

4.7 Record another Z-stack (as in Step 4.4) until the selected bead Z-profile is centered as in Fig.4.2-right.
4.8 Repeat TLens LUT calibration (steps 4.3-4.7) for the full working range, in steps of 20 μm (for finer calibration, in steps of 10 μm, so a total of 20-25 datapoints, -10, -20,-30, -40, …-240μm). An example of s-shape calibration curve is depicted in Fig.4.1.
Tips! Remember the TLens calibration must be done in one direction, otherwise a shift is expected due to hysteresis of the TLens piezo materials, as illustrated in Fig.4.3.


Fig.4.3: Hysteresis curve: optical power as function of voltage for a four-stacked TLens (average) when calibrated in different directions for two miniscopes. Measurements provided by poLight.

For Step 4b) and following steps 5-6, a distortion grid (item #m) is required, and its configuration must be adjusted to the type of objective (air/glass objective in this protocol: D0277 or lighter version D0309) and to the implantation configuration.

Distortion grid (item #m) preparation
- Add a thin layer of fluorescent marker over the second smallest grid, i.e. where the distance between closest parallel lines is 50um.
- Let it dry for 10min, then place a 1.5mm-thick cover glass on top of the marked grid with UV glue on the bottom edges of the glass and cure it to fixate it.
- Glue the grid sample to a rotator and adjust its position such it is parallel to the scope holder and miniscope (see Fig.4.4)


Fig.4.4: Example setup for distortion grid, with 20-degree angle suitable for MEC implantation.

Another method(s) to calibrate the TLens

b) Rough method using a distortion grid
i. Roughly align the distortion grid to the miniscope imaging plane.
Tips! When moving the motors up and down, the light should shift uniformly and not sideways or diagonally across the FOV.
ii. | Find the focal plane (brightest image with light in the center) and align the distortion grid to
| the cursor as shown in Fig. 4.5. On Motors Controls tab, set Zero All.
| Tips! Use a histogram by right clicking on the channel image to better visualize the pixel
distribution.
iii. | Open the TLens LUT from the widget bar. Move the TLens up from 0 to -10, and then move the z-motors down by 10μm. If the image is not yet as bright as its first, then drag the TLens
| arrows ↑ or ↓ from the TLens LUT tab until you find the same brightest focal plane.
| Tips! To move the TLens position in bigger steps, use double arrows ⇈ or ⇊.

iv. Continue moving the TLens up and the motors down in steps of 10μm, and for each plane correct the TLens LUT position as in Step3 for the whole working TLens range (typically - 200/-240μm). The calibrated curve is typically an s-shaped curve, as in Fig.4.5.

v. When calibrating the TLens, always move in one direction, otherwise there will be a shift of
| the curve for the new position as shown in Fig.4.3 (hysteresis behavior of piezo materials).


Fig.4.5: TLens calibration using a distortion grid (rough method) and typical s-shape LUT.
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

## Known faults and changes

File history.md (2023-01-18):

# History

## Version 1.2

1st International Mini2p workshop follow-up 

Updated version of 21-coupling box, with round corners to facilitate machining.
Updated version of 102-Scopebody P1 with modified surface for the dichroic mirror, without two slits sticking out but only reference points.
New Zemax (under MINI2P_toolbox\Software)files of:
a) objectives: D0213 (item 111), D0254 (item 112) and D0277 (lighter version is D0309, item 113)
b) scan lens (D0166, item 109)
c) TLens (item 114)

Minor changes to P1-Shopping & Machining List (more items added that were missing, but item ID is the same as before)
Incorporation of a few missing steps to P2-System building protocol.

Links to Mini2P video tutorials playlist:
(i) HC-920 Fiber Assembly and Integration
(ii) MINI2P Assembly Tutorial
(iii) Distortion Measurement and Distortion Correction Device
(iv) ScanImage Tutorial

## Version 1.0

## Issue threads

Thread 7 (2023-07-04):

### ISSUE TITLE
Missing P3 Assembly Protocol

### ISSUE THREAD

**Issue by jrosh** [kavli-ntnu/MINI2P_toolbox#7]
Would it be possible to provide a print version of the mini2p assembly protocol in addition to the video?

**Comment by marinesrj** [comment]
P3 - Miniscope assembly protocol has been added under https://github.com/kavli-ntnu/MINI2P_toolbox/tree/main/Protocols
It should be available shortly. Thank you.

**Comment by marinesrj** [comment]
Link to MINI2P miniscope assembly protocol : https://github.com/kavli-ntnu/MINI2P_toolbox/blob/main/Protocols/P3%20-%20Miniscope%20assembly%20protocol%20.pdf

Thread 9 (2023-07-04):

### ISSUE TITLE
Broken hyperlinks in P1 (items 60 and 62)

### ISSUE THREAD

**Issue by neurochatter** [kavli-ntnu/MINI2P_toolbox#9]
In the P1 shopping list PDF, the hyperlinks associated with Item ID 60 and 62 point to internal NTNU links. I believe these links should point to Thorlabs products as follows:
Item 60: Manual Rotation Stage (RP03/M): https://www.thorlabs.com/thorproduct.cfm?partnumber=RP03/M
Item 62: Optical post (TR75/M): https://www.thorlabs.com/thorproduct.cfm?partnumber=TR75/M

**Comment by NathanielHorne** [comment]
There are also a few broken hyperlinks on the D0166 lens, the DMSP0405 dichroic mirror, and the D0213-3X, D0254-3X, and D0277-3X objectives (items 109 - 113).
These links are broken in the sense that the links to these components lead to the homepages of the various companies they are manufactured by instead of their respective component pages.

**Comment by marinesrj** [comment]
Thank you for the corrections and suggestions. We will update the links as soon as possible in P1.
The broken hyperlinks were raised to the company main webpage, as some of them were not available in their products list because they are custom-made. However, we are going to share shortly documents with all miniature objectives, for example.

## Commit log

2021-07-30 Create Shopping and Material List.docx
2021-07-31 Update Flowchart of NETEX.png
2021-09-22 Hardware material list
    * Remove the unfinished "minimum hardware requirement"
    * Rename the Material List to no-spaces
    * Clarify cable quantities (from "8m" to "8 x 1m", this needs to be checked with W or M)
2021-09-22 Simplify hardware structure name
    [102-ScopeBody P1 .DWG, 102-ScopeBody P1 .STEP, 103-ScopeBody P2 .DWG, 103-ScopeBody P2 .STEP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]
2021-09-22 Remove version directory in Hardware
    [102-ScopeBody P1 .DWG, 102-ScopeBody P1 .STEP, 103-ScopeBody P2 .DWG, 103-ScopeBody P2 .STEP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]
2022-01-11 Modified Scope mounting module parts 74, 75 and 77
    These are updated versions of previous parts numbers #74, 75 and 77
    [74-MINI2Pholder P3 .DWG, 74-MINI2Pholder P3 .STEP, 75-MINI2Pholder P4 .DWG, 75-MINI2Pholder P4 .STEP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]
2022-01-11 compress STEP files
    Compressed all STEP files into ZIP archives
    [102-ScopeBody P1 .STEP, 103-ScopeBody P2 .STEP, 104-ScopeBody P3 .STEP, 106-Baseplate.STEP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]
2022-01-11 new folder on github to add Protocols
    to add today: Protocol S1 - shopping and material list;
    protocol S2 - MINI2P System building protocol
2022-01-11 Protocols overview
    it summarises the main protocols, including links to the video tutorials (MINI2P assembly). It still lacks HC-920 video link, generated by Nienke tomorrow morning
2022-01-11 LUT laser and MDFs
    laser calibration table
    MDF 2000HZ
    MDF 5600Hz
2022-01-11 change name
    [21-CouplingBox .DWG, 22-Cup .DWG, 23-CouplingHolder .DWG, 24-CollimatorProtector .DWG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]
2022-01-11 comments to LUT laser
    added comments explaining the 920 nm AOM beamlut
2022-01-12 21-coupling box add SM05
    SM05 on the front was lacking on 21 drawing (essential when ordering parts to 3A prototype)
    [21-CouplingBox .DWG]
2022-01-25 Updated links of HC-920 assembly
    Added links of video tutorials
2022-01-31 Replaced previous 103
    previous version 103 changed (e.g. height from 5.92to 7.96mm)
    [103-ScopeBody P2 .DWG, 103-ScopeBody P2 .STEP]
2022-01-31 Reduce confusion headbar MEC-v2
    add dimensions of outer and inner diameter, as 3A was confused last time (Sep2022)
    [HeadBar_MEC_5mm.DWG]
2022-01-31 Compressing updated 103 step file
    update zip files
    [103-ScopeBody P2 .STEP]
2022-02-09 update drawings name cup to cap
    [22-Cap .DWG, 28-ControlBoxCap .DWG]
2022-02-14 update latest version of headbar
    [HeadBar_MEC_5mm.DWG]
2022-03-17 add missing files
    Glass rods(32), glass flange(33)
    [32-GlassRods_ZF62 .DWG, 33-GlassFlange .DWG]
2022-03-17 all miniscope parts put together in an assembly (step file)
2022-03-17 add DM part no 110
    still need to add Scan lens, objectives, among others at a later stage
    [110-DM.DWG]
2022-03-17 74-MINI2Pholder P3 small modification
    enlarge holes from 3.5 to 3.5 on the 3D drawing, even though it was correct on the 2D drawing.
    [74-MINI2Pholder P3 .DWG]
2022-03-18 Update 2S drawings
    Added customized components
    [110-DM.DWG, 110-DM.STEP, 32-GlassRods_ZF62 .DWG, 32-GlassRods_ZF62 .STEP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]
2022-03-18 Update hardware
    [32-GlassRods_ZF62 .DWG, 33-GlassFlange .DWG]
2022-03-28 Upload the MEMS PCB
2022-03-28 The first version of MINI2P SI device
    This MINI2P SI device enables users to measure MINI2P distortion in different plane, do the fast data correction, and register MINI2P system information in ScanImage software. And all these informati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
2022-04-12 Corrected 75-holder pdf and dwg
    [75-MINI2Pholder P4 .DWG]
2022-04-19 Update P1 - Shopping & Machining List .pdf
    add material info on 3A parts
2022-05-02 corrected name of part 24
    coupling protector (not collimator protector)
    [24-CouplingProtector .DWG]
2022-09-09 Update P2 - System building protocol .pdf
    replace glue typo
2022-09-12 Update P1 - Shopping & Machining List .pdf
    update material coupling protector
2022-11-19 Cleaning repository
    Removing improperly licenced data from the repository
    [110-DM.STEP]
2022-12-16 update item 21 coupling box
    round corners after drawing 20221120
    compress to zipped folder
    [21-CouplingBox .DWG, 21-CouplingBox_20221120.DWG]
2022-12-16 new version 102 scopebody P1
    updated without slits sticking out 20220912
    [102-ScopeBody P1 - new version_20220912.DWG, 102-ScopeBody P1 .DWG]
2022-12-16 update P2 system building protocol
    added step with heat gun/fiber prep
2022-12-16 Zemax files (scan lens objectives)
    only scan lens and objectives
    D0166, D0213, D0277, D0239, D0254
2022-12-16 history updated after Zemax
    remove collimating lens
2022-12-16 Update README.md
    added link to video - mini2p assembly
2023-01-18 Apply changes post 2022-12 Mini2p Workshop (#8)
    * history simplified
    Update history with new changes, but not yet including some Zemax files and not including generic MDFs (because it needs testing)
    * update item 21 coupling box
    * new version 102 scopebody P1
    * update protocol P1 shopping and machining
    add a few missing items
    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
    [102-ScopeBody P1 - new version_20220912.DWG, 102-ScopeBody P1 .DWG, 21-CouplingBox .DWG, 21-CouplingBox_20221120.DWG]
2023-05-30 P1 updated
    Specific parts to items 30 related to GFB solution. New version of scopebody P3 adapted to GFB, and other adapter to old TFB (sub-items under 104). Finally, examples of suppliers to Femtosecond laser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
    [Adapter for old TFB.DWG, Adapter for old TFB.STEP, GFBholder.DWG, GFBholder.STEP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]
2023-05-31 New GFB with protocol and models (#12)
    * update P2 system building protocol
    * Zemax files (scan lens objectives)
    * history updated after Zemax
    *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
    [Adapter for old TFB.DWG, Adapter for old TFB.STEP, GFBholder.DWG, GFBholder.STEP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]
2023-06-01 Update GFB Assembly Protocol .pdf
    minor fix of typos and clearer illustration of dead cores.
2023-06-01 Post workshop (#13)
    * Update README.md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
2023-06-27 Added link to GFB assembly protocol pdf
2023-07-03 Create P3 - Miniscope assembly protocol .pdf
    Miniscope assembly protocol of MINI2P 2022
2023-07-03 new protocol MEMS wires and mirror
    also update links of video-tutorials under Protocol overview
2023-07-03 Update README.md (#14)
    update link that leads to last version of P1 - shopping machining list for new detection fiber solution, GFB see Items 30, and 104. Updated laser suppliers in items 29 & 93: new example of suppliers 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
2023-07-14 dummy scope
    3D model and 2D drawings of dummy scope to fixate to the baseplate.
    [Dummy.DWG, Dummy.STEP]
2023-08-03 Replace MDFs and remove Distortion correction functions
    MDFs for L-FOV (2000Hz) and F-FOV (5600Hz) MEMS with updated settings suitable for both miniscope versions, 2022 and 2023.
    Removed Distortion correction functions which are replaced by MINI2P SI Device available in another folder.
2023-08-03 MINI2P 2023 assembly protocol and others updated accordingly
    New P3-MINI2P 2023 assembly protocol, and others updated accordingly, especially P1-Shopping Machining list. Also, new system operate instruction protocol.
    [2207021030-Catalog for mini objectives .xlsx]
2023-08-03 New 3D/2D models of MINI2P 2023
    [102-ScopeBody P1 - new version_20220912.DWG, 103-ScopeBody P2 .DWG, 104-ScopeBody P3 .DWG, 107-AlignmentTool.DWG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]
2023-08-03 Removal of mini2p 2022 models
    [102-ScopeBody P1 - new version_20220912.DWG, 103-ScopeBody P2 .DWG, 104-ScopeBody P3 .DWG, 107-AlignmentTool.DWG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]
2023-08-03 Mini2p2023 (#22)
    * Replace MDFs and remove Distortion correction functions
    * MINI2P 2023 assembly protocol and others updated accordingly
    * New 3D/2D models of MINI2P 2023
    * Removal of mini2p 2022 models
    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
    [102-ScopeBody P1 - new version_20220912.DWG, 103-ScopeBody P2 .DWG, 104-ScopeBody P3 .DWG, 107-AlignmentTool.DWG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]
2023-08-16 Standard performance testing protocol
    Add new protocol that includes preliminary testing of a MINI2P system and miniscope calibration: Z-resolution, TLens calibration, estimate FOV and distortion detection and correction
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2023-10-20 200um shift stitching adapters
    added 200um shift stitching adapters and shorter than original version
    [Scopebody adapter_V2_lateralshifting_ML+200_AP+200 .stp, Scopebody adapter_V2_lateralshifting_ML+200_AP+200.dwg, Scopebody adapter_V2_lateralshifting_ML+200_AP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]
2023-10-23 reorganize folders of stitching adapters in types
    400um shifted stitching adapters
    (there is also smaller shift, 200um and shorter 200um)
    [Scopebody adapter_V2_lateralshifting_ML+0400_AP+0400.DWG, Scopebody adapter_V2_lateralshifting_ML+0400_AP+0800.DWG, Scopebody adapter_V2_lateralshifting_ML+040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]
2023-10-23 200um shift stitching adapters
    3D models of 200um shift stitching adapters
    [Scopebody adapter_V2_lateralshifting_ML+200_AP+200.STEP, Scopebody adapter_V2_lateralshifting_ML+200_AP-200.STEP, Scopebody adapter_V2_lateralshifting_ML+200_A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]
